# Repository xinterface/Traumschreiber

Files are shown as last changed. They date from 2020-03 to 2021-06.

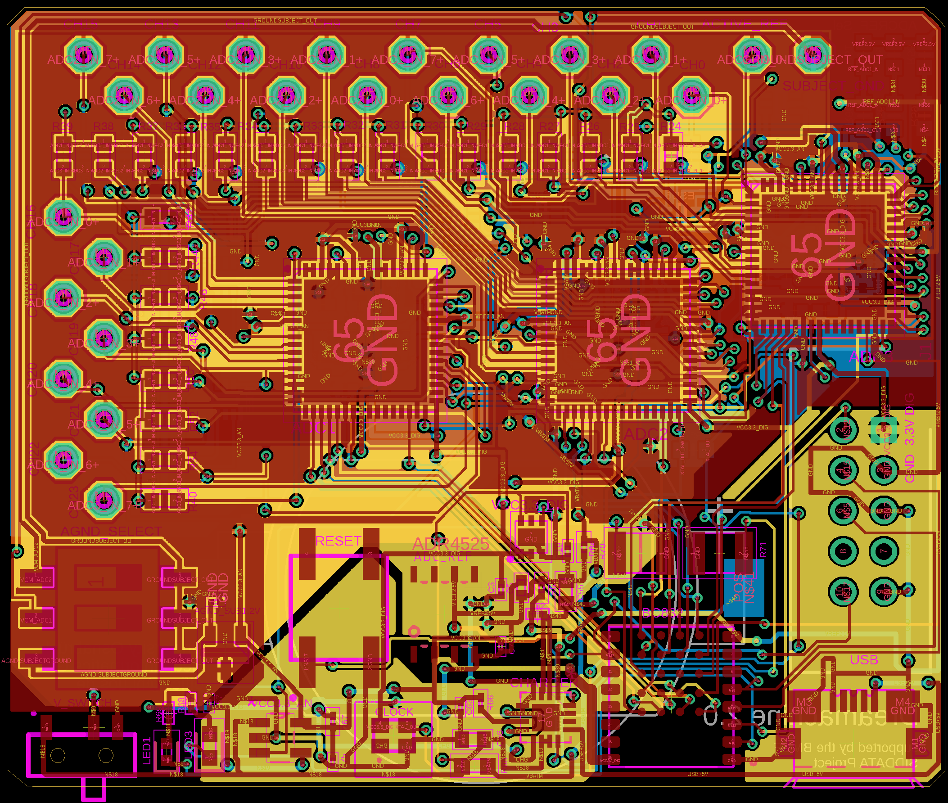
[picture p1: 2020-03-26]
Board_Design/Design_V2.1 - Final/d/Board2.0.png

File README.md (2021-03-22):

# Traumschreiber
Repository of the Traumschreiber and all affiliated projects and theses

## Thus far, this includes:

- A collection of theses
- The repos of the two projects concerned with App Design for the Traumschreiber. More information [on EEGDroid](https://github.com/neuroinfo-os/Traumschreiber/blob/master/Theses/App%20Development/RojasCampos_AppRecordStoreManageEEG.pdf) and on [Traumschreiber mobile EEG](https://github.com/neuroinfo-os/Traumschreiber/blob/master/Theses/Event%20Related%20Potentials/Vidal_AuditoryEvokedPotentials.pdf)
- A collection of operation manuals of the hardware components
- In Progress: Streaming implementation
- In Progress: Embedded System and BLE
# Traumschreiber's List (Version 2.8) + (Version EEG_v2_92_X25)
https://docs.google.com/spreadsheets/d/1prQXEEBJC7Lh-TTywT1AkwJn4IeFenbX4uT630RnToc/edit#gid=0

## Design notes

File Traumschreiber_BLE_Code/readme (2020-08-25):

Compilation and programming the Traumschreiber were tested with Segger Embedded Studio (SES).
https://www.segger.com/downloads/embedded-studio

for compiling one needs the Nordic SDK 15.3
https://www.nordicsemi.com/Software-and-tools/Software/nRF5-SDK/Download
(downloading it with only softdevice s132 is sufficient for use with Traumschreiber)

to compile the code:
- store code folder in the SDK folder at:
SDK/examples/ble_peripheral
- open SES
- choose File -> 'open solution' and navigate to:
SDK/examples/ble_peripheral/<code folder>/pca10040/s132/ses/
- and click the .em-file

the main files are
main.c
traumschreiber_service.c/.h
ad_spi.c/.h

to programm the Traumschreiber:
- compile the project in SES (I use the key F7, should show two partly green bars on the bottom when finished)
- connect the programming board and connect the Traumschreiber to that one with the grey 10-Pin-Connector
- switch the Traumschreiber on!!!!
- use 'Target' -> 'Connect J-Link'
- use 'Target' -> 'Download ble_app_...'
during programming the Traumschreiber LEDs should be off. when finished it should be on.

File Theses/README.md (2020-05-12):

# Traumschreiber
The Traumschreiber system is the subject of several theses covering different research areas within Cognitive Science and Neuroinformatics. Here, the theses are collected. The following gives a brief summary of the individual projects.

#### _The Traumschreiber System - Enabling Crowd-based, Automated, Complex, Polysomnographic Sleep and Dream Experiments_ - K. Appel, Dissertation

In this dissertation the development of the Traumschreiber System as well as its evaluation is presented. The high-tech sleep mask was developed to enable naive crowd
subjects to perform complex polysomnographic sleep and dream experiments at home. It is shown that on the one hand the quality of polysomnographic data recording – including measurements of EEG, EOG, EMG and ECG–, can compete with commercial medical sleep laboratory systems. On the other hand, it was shown with two field studies that even novice subjects can conduct sleep experiment at their homes with the Traumschreiber.

## App Development

#### _Design and implementation of an Android app to  record, store and manage EEG signals_ - R. A. Rojas Campos, Master's Thesis (August 2019)

This thesis describes the most advanced Traumschreiber app to date. With the Android app, the user can collect, plot, save, manage, and share EEG sessions, recorded with the Traumschreiber system. It furthermore introduces a chatbot expert, used to inform the user about epilepsy and presents general information about epilepsy in a clear and accessible way. The code is available [in this repository](https://github.com/adrocampos/EEG-Droid).

#### _Developing and designing a mediator smartphone application for portable sleep EEG recording and biofeedback with focus on the end user experience_ - M. Jäkel, Bachelor's Thesis (February 2017)

This thesis reports on the implementation of a prototype Android application that introduces users to the sleep mask. With the app, users can, among other, connect the Traumschreiber via Bluetooth to their phones, enabling them to visualize recorded EEG data.

## Detection of Event Related Potentials with the Traumschreiber

#### _Studying Neural Correlates of Mind Wandering with Mobile EEG_ - M. Bammel, Bachelor's Thesis (April 2020)

This thesis constitutes a replication of a study by Braboszez and Delorme (2011) who identified neural markers of low alertness during mind wandering with the Traumschreiber. The experiments expose a significantly decreased alpha and beta frequency band power during mind wandering. However, the replication demonstrates that studying higher cognitive functions in a mobile setup using the Traumschreiber does not yield equivalent results compared to a stationary research graded EEG system. The full sourcecode of the project is available [in the author's repository](https://github.com/mbammel/BscThesis).

#### _Auditory Evoked Potentials with Mobile EEG_ - M. Vidal De Palol, Master's Thesis (March 2019)

This project combines the development of an Android App for real-time EEG visualization and recording and an experiment to assess the capability of the device for recording Auditory Evoked Potentials.

#### _Measuring vMMN, P300 and AEPs with a mobile EEG system_ - M. Reimann, Bachelor's Thesis (September 2018)

Within this thesis the potential of the Traumschreiber as mobile EEG system is explored by evaluating its usability and ability to detect event-related potentials (ERP). It is shown that the device is able to produce good and very good results for the ERP under consideration.

#### _Analyzing event-related potentials in 8-channel EEG data using machine learning methods_ - A.-K. Schalkamp, Bachelor's Thesis (September 2018)

This thesis describes a study performed to evaluate whether EEG data acquired with the Traumschreiber can be used with traditional and single-trial analysis. Furthermore, it expands on the importance of electrode placement.

## Eye Position and Gaze Estimation

#### _Eye gaze estimation and gesture recognition using mobile EEG, An application for sleep communication_ - V. Amo Olea, Master's Thesis (September 2019)

Within this project a real-time eye-gaze estimation and gesture recognition
system using Electrooculography (EOG) was developed. A Convolutional Neural Net was trained to recognize eye-typing gestures and three command gestures from movement with closed eyes.

#### _Extracting Eye Positions from Electrooculographic Recordings Using a Machine Learning Approach_ - F. Laubisch, Bachelor's Thesis (September 2016)

In this thesis the relationship between EOG data provided by the Traumschreiber and eye position obtained with a wearable eye tracking device is assessed. It is shown that the sole EOG data is not yet sufficient to produce reliable eye tracking information.

## Sleep and Lucid Dreaming Research

#### _Conducting a Polysomnographic, Automated Auditory Stimulation Sleep Experiment Using a Portable High-Tech Sleep Mask_ - L.S. Mandt, Bachelor's Thesis (April 2017)
The field study discussed in this thesis evaluates the portable high-tech sleep mask for home-based sleep experiments using polysomnography. Additionally, it examines whether the arousal threshold of individual participants can be determined by exposing them to auditory stimulation during the night.

#### _The Scienticity of Lucid Dream Research - A Theoretical and Empirical Approach_ - K. Lüth, Bachelor's Thesis (July 2015)

This work discusses the science-theoretical and historical background of lucid dream research. It presents a survey concerned with the attitude the public has towards the field. The survey showed that the public has a positive opinion.

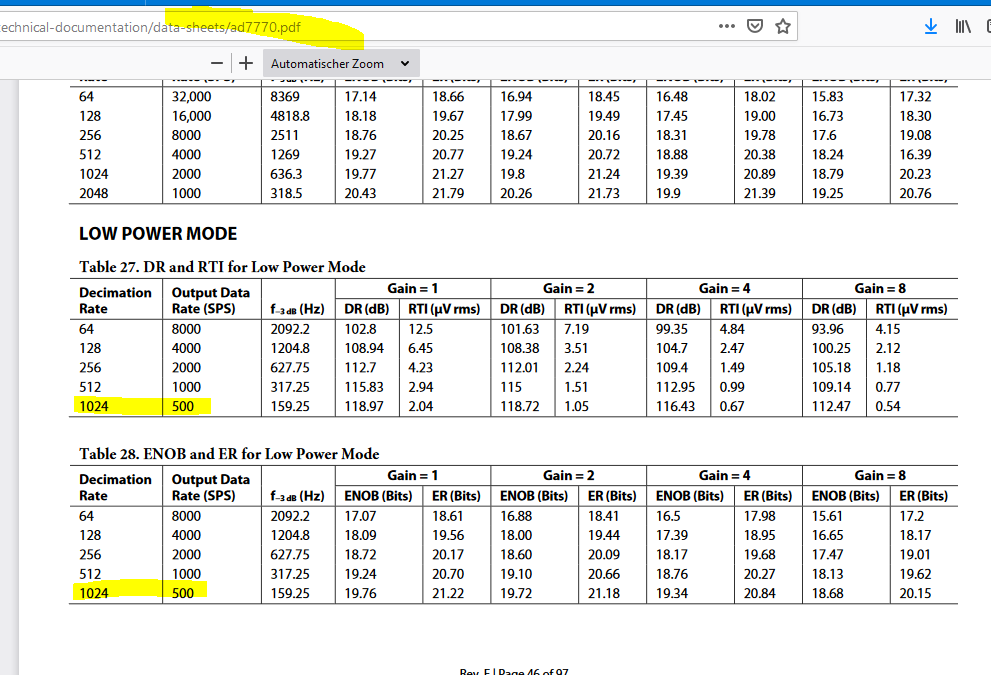
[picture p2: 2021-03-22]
Board_Design/Design_V3.10/PDFs/7770_decimation_rate.PNG

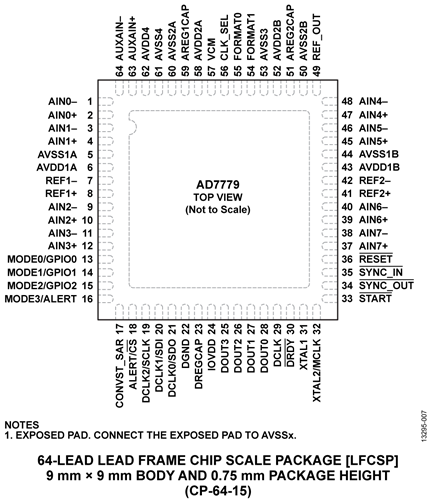
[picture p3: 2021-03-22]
Board_Design/Design_V3.10/PDFs/AD7779-pc.png

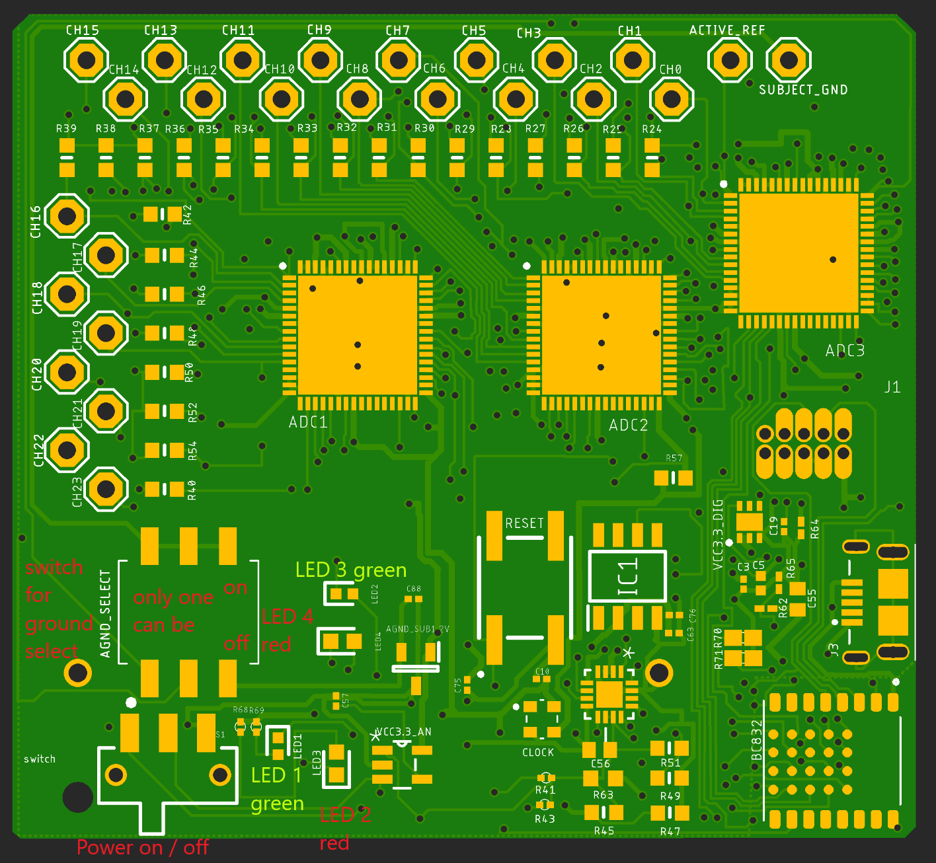
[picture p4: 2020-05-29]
Board_Design/Design_V2.9x/board-explain.png

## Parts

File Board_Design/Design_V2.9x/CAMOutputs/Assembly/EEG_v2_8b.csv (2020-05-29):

Qty | Value | Device | Package | Parts | Description | ALLIED_NUMBER | ALLIED_PRICE-STOCK | AVAILABILITY | CENTERLINE_PITCH | COMMENT | DESCRIPTION | HEIGHT | MANUFACTURER_NAME | MANUFACTURER_PART_NUMBER | MF | MOUSER_PART_NUMBER | MOUSER_PRICE-STOCK | MP | MPN | NUMBER_OF_POSITIONS | OC_FARNELL | OC_NEWARK | PACKAGE | POPULARITY | PRICE | PRODUCT_TYPE | RS_PART_NUMBER | RS_PRICE-STOCK | SUPPLIER | TE_PURCHASE_URL
58 | 0 Ohm | CRCW06030000Z0EAC | RESC1608X55N | R1, R2, R3, R4, R5, R6, R7, R8, R9, R10, R11, R12, R13, R14, R15, R16, R17, R18, R19, R20, R21, R22, R23, R24, R25, R26, R27, R28, R29, R30, R31, R32, R33, R34, R35, R36, R37, R38, R39, R40, R42, R44, R45, R46, R47, R48, R49, R50, R51, R52, R54, R55, R56, R57, R58, R59, R60, R61 | Thick Film Resistors - SMD |  |  |  |  |  | Thick Film Resistors - SMD | 0.55mm | Vishay | CRCW06030000Z0EAC |  | 71-CRCW06030000Z0EAC | https://www.mouser.com/Search/Refine.aspx?Keyword=71-CRCW06030000Z0EAC
2 | 0.01uF | GRM033R61E103MA12J | CAPC0603X33N | C10, C57 | Multilayer Ceramic Capacitors MLCC - SMD/SMT 0201 0.01uF 25volts *Derate Voltage/Temp |  |  |  |  |  | Multilayer Ceramic Capacitors MLCC - SMD/SMT 0201 0.01uF 25volts *Derate Voltage/Temp | 0.33mm | Murata Electronics | GRM033R61E103MA12J |  | 81-GRM033R61E103MA2J | https://www.mouser.co.uk/ProductDetail/Murata-Electronics/GRM033R61E103MA12J?qs=hNud%2FORuBR1kPmeKqdhtJA%3D%3D
25 | 0.1 uF | LMK063C6104KP-F | CAPC0603X33N | C63, C64, C65, C66, C67, C68, C69, C70, C71, C72, C73, C74, C75, C76, C77, C78, C79, C81, C82, C83, C84, C85, C86, C87, C88 | 0201 (0603M), 0402 (1005M) 100nF MLCC 10V dc +/-10% SMD LMK063C6104KP-F |  |  |  |  |  | 0201 (0603M), 0402 (1005M) 100nF MLCC 10V dc +/-10% SMD LMK063C6104KP-F | 0.33mm | TAIYO YUDEN | LMK063C6104KP-F |  | 963-LMK063C6104KP-F | https://www.mouser.co.uk/ProductDetail/Taiyo-Yuden/LMK063C6104KP-F?qs=vF%252B8ahGVildHIKWi2d6PKQ%3D%3D |  |  |  |  |  |  |  |  |  | 1843409P | http://uk.rs-online.com/web/p/products/1843409P
3 | 1 kohm | RC0201JR-071KL | RESC0603X26N | R41, R43, R69 | YAGEO - RC0201JR-071KL - RES, THICK FILM, 1K, 5%, 0.5W, 0201, REEL |  |  |  |  |  | YAGEO - RC0201JR-071KL - RES, THICK FILM, 1K, 5%, 0.5W, 0201, REEL | 0.26mm | YAGEO (PHYCOMP) | RC0201JR-071KL |  | 603-RC0201JR-071KL | https://www.mouser.co.uk/ProductDetail/Yageo/RC0201JR-071KL?qs=V1yeUXFNrklkaJ2L0z8I%252BA%3D%3D |  |  |  |  |  |  |  |  |  | 1987634 | http://uk.rs-online.com/web/p/products/1987634
31 | 1 uF | JMK105BJ105MP-F | CAPC1005X33N | C1, C2, C4, C5, C6, C7, C8, C9, C11, C12, C13, C14, C15, C16, C17, C18, C21, C24, C25, C26, C27, C28, C29, C30, C31, C32, C37, C38, C39, C40, C51 | Taiyo Yuden JMK105BJ105MP-F 1F MLCC 6.3V dc +/-20% Tolerance SMD |  |  |  |  |  | Taiyo Yuden JMK105BJ105MP-F 1F MLCC 6.3V dc +/-20% Tolerance SMD | 0.33mm | TAIYO YUDEN | JMK105BJ105MP-F |  | 963-JMK105BJ105MP-F | https://www.mouser.com/Search/Refine.aspx?Keyword=963-JMK105BJ105MP-F |  |  |  |  |  |  |  |  |  | 1843471 | https://uk.rs-online.com/web/p/products/1843471
2 | 10 uF | EMK107BBJ106MA-T | CAPC1608X100N | C55, C56 | TAIYO YUDEN - EMK107BBJ106MA-T - CAPACITOR, MLCC, X5R, 10UF, 16V, 0603, REEL |  |  |  |  |  | TAIYO YUDEN - EMK107BBJ106MA-T - CAPACITOR, MLCC, X5R, 10UF, 16V, 0603, REEL | 1mm | TAIYO YUDEN | EMK107BBJ106MA-T |  | 963-EMK107BBJ106MA-T | https://www.mouser.com/Search/Refine.aspx?Keyword=963-EMK107BBJ106MA-T |  |  |  |  |  |  |  |  |  | 1843904P | http://uk.rs-online.com/web/p/products/1843904P
1 | 1051 | 1051 | 1051 | U2 | Cylindrical Battery Contacts, Clips, Holders & Springs THM BATTERY HOLDER CR123A | 71135178 | https://www.alliedelec.com/keystoneelectronics-1051/71135178/ |  |  |  | Cylindrical Battery Contacts, Clips, Holders & Springs THM BATTERY HOLDER CR123A | 15.24mm | Keystone Electronics | 1051 |  | 534-1051 | https://www.mouser.co.uk/ProductDetail/Keystone-Electronics/1051?qs=wOxb8XianXhV6wGCGUD6gA%3D%3D
2 | 150060RS75000 | 150060RS75000 | LEDC1608X80N | LED3, LED4 | WURTH ELEKTRONIK - 150060RS75000 - LED, 0603, RED, 250MCD, 625NM |  |  |  |  |  | WURTH ELEKTRONIK - 150060RS75000 - LED, 0603, RED, 250MCD, 625NM | 0.8mm | Wurth Elektronik | 150060RS75000 |  | 710-150060RS75000 | https://www.mouser.com/Search/Refine.aspx?Keyword=710-150060RS75000 |  |  |  |  |  |  |  |  |  | 8154203P | http://uk.rs-online.com/web/p/products/8154203P
1 | 1kohm | RC0201JR-071KL | RESC0603X26N | R68 | YAGEO - RC0201JR-071KL - RES, THICK FILM, 1K, 5%, 0.5W, 0201, REEL |  |  |  |  |  | YAGEO - RC0201JR-071KL - RES, THICK FILM, 1K, 5%, 0.5W, 0201, REEL | 0.26mm | YAGEO (PHYCOMP) | RC0201JR-071KL |  | 603-RC0201JR-071KL | https://www.mouser.co.uk/ProductDetail/Yageo/RC0201JR-071KL?qs=V1yeUXFNrklkaJ2L0z8I%252BA%3D%3D |  |  |  |  |  |  |  |  |  | 1987634 | http://uk.rs-online.com/web/p/products/1987634
2 | 2.2 kOhms | RC0603JR-072K2L | RESC1608X55N | R70, R71 | RESISTOR, 0603 2.2K Ohms +/-5% 1/10 W |  |  |  |  |  | RESISTOR, 0603 2.2K Ohms +/-5% 1/10 W | 0.55mm | YAGEO (PHYCOMP) | RC0603JR-072K2L |  | 603-RC0603JR-072K2L | https://www.mouser.co.uk/ProductDetail/Yageo/RC0603JR-072K2L?qs=%2F9ZTgpVJnN4N31C%252B33L1Sw%3D%3D
2 | 2.2uF | GRM033R60J225ME47D | CAPC0603X33N | C3, C19 | Multilayer Ceramic Capacitors MLCC - SMD/SMT 0201 2.2uF 6.3volts |  |  |  |  |  | Multilayer Ceramic Capacitors MLCC - SMD/SMT 0201 2.2uF 6.3volts | 0.33mm | Murata Electronics | GRM033R60J225ME47D |  | 81-GRM033R60J225ME7D | https://www.mouser.com/Search/Refine.aspx?Keyword=81-GRM033R60J225ME7D
1 | 200kohm | CRCW0201200KFNED | RESC0603X28N | R62 | VISHAY - CRCW0201200KFNED - RES, THICK FILM, 200K, 1%, 0.05W, 0201 |  |  |  |  |  | VISHAY - CRCW0201200KFNED - RES, THICK FILM, 200K, 1%, 0.05W, 0201 | 0.28mm | Vishay | CRCW0201200KFNED |  | 71-CRCW0201200KFNED | https://www.mouser.co.uk/ProductDetail/Vishay-Dale/CRCW0201200KFNED?qs=4bbongekVIR3iw5xFt9eBQ%3D%3D
1 | 2040002-1 | 2040002-1 | TE_2040002-1 | J3 | Conn USB Type B RCP 5 POS 0.65mm Solder RA SMD 5 Terminal 1 Port T/R |  |  | Unavailable | .65 mm[.025 in] | 2040002-1 | Conn Micro USB 2.0 Type B RCP 5 POS 0.65mm Solder RA SMD 5 Terminal 1 Port T/R |  |  |  | TE Connectivity |  |  | 2040002-1 |  | 5 |  |  | None |  | None | Connector |  |  |  | https://www.te.com/usa-en/product-2040002-1.html?te_bu=Cor&te_type=disp&elqCampaignId=32493
1 | 219-3LPSTR | 219-3LPSTR | 2193LPSTR | AGND_SELECT | 3 Way Surface Mount DIP Switch Single Pole Single Throw (SPST) |  |  |  |  |  | 3 Way Surface Mount DIP Switch Single Pole Single Throw (SPST) | 3.95mm | CTS | 219-3LPSTR |  | 774-2193LPSTR | https://www.mouser.com/Search/Refine.aspx?Keyword=774-2193LPSTR |  |  |  |  |  |  |  |  |  | 1774327 | http://uk.rs-online.com/web/p/products/1774327
2 | 41.2 kOhms | CRCW020141K2FNED | RESC0603X28N | R64, R65 | Thick Film Resistors - SMD 41.2K OHM 1% |  |  |  |  |  | Thick Film Resistors - SMD 41.2K OHM 1% | 0.28mm | Vishay | CRCW020141K2FNED |  | 71-CRCW020141K2FNED | https://www.mouser.com/Search/Refine.aspx?Keyword=71-CRCW020141K2FNED
1 | 82kOhms | ERA-3AEB823V | RESC1608X55N | R63 | RESISTOR, 0603 82 kOhm +/-0.1% 0.1 W |  |  |  |  |  | RESISTOR, 0603 82 kOhm +/-0.1% 0.1 W | 0.55mm | Panasonic | ERA-3AEB823V |  | 667-ERA-3AEB823V | https://www.mouser.com/Search/Refine.aspx?Keyword=667-ERA-3AEB823V
3 | AD7771BCPZ | AD7771BCPZ | QFN50P900X900X80-65N | ADC1, ADC2, ADC3 | Analog to Digital Converters - ADC Eight 24B 128ksps SD-ADC PGA SRC |  |  |  |  |  | Analog to Digital Converters - ADC Eight 24B 128ksps SD-ADC PGA SRC | 0.8mm | Analog Devices | AD7771BCPZ |  | 584-AD7771BCPZ | https://www.mouser.com/Search/Refine.aspx?Keyword=584-AD7771BCPZ
1 | ADP7118ACPZN3.3-R7 | ADP7118ACPZN3.3-R7 | SON65P200X200X65-7N | VCC3.3_DIG | LDO Voltage Regulators 20V 200mA LDO 3.3Vo |  |  |  |  |  | LDO Voltage Regulators 20V 200mA LDO 3.3Vo | 0.65mm | Linear Technology | ADP7118ACPZN3.3-R7 |  | 584-P7118ACPZN3.3R7 | https://www.mouser.com/Search/Refine.aspx?Keyword=584-P7118ACPZN3.3R7
1 | ADR4525ARZ | ADR4525ARZ | SOIC127P600X175-8N | IC1 | Analog Devices, ADR4525ARZ Analog Devices ADR4525ARZ, Series Voltage Reference 2.5V, /-0.02% 15 V max., 8-Pin SOIC |  |  |  |  |  | Analog Devices, ADR4525ARZ Analog Devices ADR4525ARZ, Series Voltage Reference 2.5V, /-0.02% 15 V max., 8-Pin SOIC | 1.75mm | Analog Devices | ADR4525ARZ |  | 584-ADR4525ARZ | https://www.mouser.co.uk/ProductDetail/Analog-Devices/ADR4525ARZ?qs=WIvQP4zGangC7PeS%252B5s%2F2Q%3D%3D |  |  |  |  |  |  |  |  |  | 8023880P | http://uk.rs-online.com/web/p/products/8023880P
1 | BC832 | BC832 | XCVR_BC832 | BC832 | Micro BLE 5 Module: Nordic nRF52832 SoC with chip antenna and castellated pins |  |  | Unavailable |  |  | Bluetooth Bluetooth v5.0 Transceiver Module 2.4GHz Integrated, Chip Surface Mount |  |  |  | Fanstel Corp. |  |  | BC832 |  |  |  |  | Module Fanstel Corp. |  | None
1 | BQ24072TRGTR | BQ24072TRGTR | QFN50P300X300X100-17N | CHARGER | 1.5A USB-Friendly Li-Ion Battery Charger and Power-Path Management IC |  |  |  |  |  |  |  |  |  |  |  |  |  | BQ24072TRGTR |  | - | 74R6078 | QFN-16 |  |  |  |  |  | Texas Instruments
1 | DSC1001DI5-008.1920T | DSC1001DI5-008.1920T | DSC1001DI50081920T | CLOCK | Standard Clock Oscillators MEMS Oscillator, Low Power, -40C-85C, 10ppm 1.8V-3.3V Low-Power Precision CMOS Oscillators |  |  |  |  |  | Standard Clock Oscillators MEMS Oscillator, Low Power, -40C-85C, 10ppm 1.8V-3.3V Low-Power Precision CMOS Oscillators | 0.85mm | Microchip | DSC1001DI5-008.1920T |  | 998-1001DI5008.1920T | https://www.mouser.co.uk/ProductDetail/Microchip-Technology-Micrel/DSC1001DI5-0081920T?qs=moDRE%2FDosU0uLfPLWfhb9w%3D%3D
1 | EVQ-Q2B03W | EVQ-Q2B03W | EVQQ2 | RESET | PANASONIC ELECTRONIC COMPONENTS - EVQ-Q2B03W - SWITCH, TACTILE, SPST-NO, 20mA, 15VDC, SMD | 70270748 | https://www.alliedelec.com/panasonic-evq-q2b03w/70270748/ |  |  |  | PANASONIC ELECTRONIC COMPONENTS - EVQ-Q2B03W - SWITCH, TACTILE, SPST-NO, 20mA, 15VDC, SMD | mm | Panasonic | EVQ-Q2B03W |  | 667-EVQ-Q2B03W | https://www.mouser.com/Search/Refine.aspx?Keyword=667-EVQ-Q2B03W
1 | ISL21010DFH312Z-TK | ISL21010DFH312Z-TK | SOT95P237X112-3N | AGND_SUB1.2V | Voltage References Micropower Voltage Reference |  |  |  |  |  | Voltage References Micropower Voltage Reference | 1.12mm | Renesas Electronics | ISL21010DFH312Z-TK |  | 968-ISL21010DFH312ZT | https://www.mouser.com/Search/ProductDetail.aspx?qs=9fLuogzTs8LVsLxgRfQnrw%3d%3d
1 | JS102011SAQN | JS102011SAQN | JS102011SAQN | S1 | C & K COMPONENTS - JS102011SAQN - SWITCH, SPDT, 0.6A, 6VDC, SIDE, SMD | 71173976 | https://www.alliedelec.com/c-k-js102011saqn/71173976/ |  |  |  | C & K COMPONENTS - JS102011SAQN - SWITCH, SPDT, 0.6A, 6VDC, SIDE, SMD | mm | C & K COMPONENTS | JS102011SAQN |  | 611-JS102011SAQN | https://www.mouser.com/Search/Refine.aspx?Keyword=611-JS102011SAQN |  |  |  |  |  |  |  |  |  | 1543603 | http://uk.rs-online.com/web/p/products/1543603
26 | SE11 | SE11 | SE11 | ACTIVE_REF, CH0, CH1, CH2, CH3, CH4, CH5, CH6, CH7, CH8, CH9, CH10, CH11, CH12, CH13, CH14, CH15, CH16, CH17, CH18, CH19, CH20, CH21, CH22, CH23, SUBJECT_GND | SOLDER PAD RTM, drill 1,1mm, distributor Buerklin, 07F810 |  |  |  |  |  |  |  |  |  |  |  |  |  |  |  |  |  |  | 2
1 | SHF-105-01-L-D-TH-TR | SHF-105-01-L-D-TH-TR | SHF10501LDTHTR | J1 | Headers & Wire Housings .050 Shrouded Terminal Strip For FFSD" |  |  |  |  |  | Headers & Wire Housings .050 Shrouded Terminal Strip For FFSD" | 5.33mm | SAMTEC | SHF-105-01-L-D-TH-TR |  | 200-SHF10501LDTHTR | https://www.mouser.co.uk/ProductDetail/Samtec/SHF-105-01-L-D-TH-TR?qs=%252BZP6%2F%252BtExtDFuyepp9uTfQ%3D%3D
2 | SML-P11MTT86R | SML-P11MTT86R | LEDC1006X25N | LED1, LED2 | ROHM - SML-P11MTT86R - LED, YELLOW GREEN, 2.1MCD, 569NM, 0402 |  |  |  |  |  | ROHM - SML-P11MTT86R - LED, YELLOW GREEN, 2.1MCD, 569NM, 0402 | 0.25mm | ROHM Semiconductor | SML-P11MTT86R |  | 755-SML-P11MTT86R | https://www.mouser.com/Search/Refine.aspx?Keyword=755-SML-P11MTT86R
7 | TPD4E1B06DRLR | TPD4E1B06DRLR | SOP50P160X60-6N | ESD1, ESD2, ESD3, ESD4, ESD5, ESD6, ESD7 | Bidirectional Quad-Channel High-Speed ESD Protection Device |  |  |  |  |  | Bidirectional Quad-Channel High-Speed ESD Protection Device | 0.6mm | Texas Instruments | TPD4E1B06DRLR |  | 595-TPD4E1B06DRLR | https://www.mouser.com/Search/Refine.aspx?Keyword=595-TPD4E1B06DRLR
1 | TPS73233DBVT | TPS73233DBVT | SOT95P280X145-5N | VCC3.3_AN | Cap-Free, NMOS, 250mA Low Dropout Regulator with Reverse Current Protection |  |  |  |  |  |  |  |  |  |  |  |  |  | TPS73233DBVT |  | - | 87H2968 | SOT-23-5 |  |  |  |  |  | Texas Instruments

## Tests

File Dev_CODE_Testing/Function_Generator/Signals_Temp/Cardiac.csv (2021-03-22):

data lenth | 16384
frequency | 1000.000000000
amp | 4.000000000
offset | 0.000000000
phase | 0.000000000
xpos | value
0.000000e+000 | 0.00000
6.103516e-008 | 0.00562
1.220703e-007 | 0.00562
1.831055e-007 | 0.00562
2.441406e-007 | 0.00562
3.051758e-007 | 0.00562
3.662109e-007 | 0.00562
4.272461e-007 | 0.00562
4.882813e-007 | 0.00562
5.493164e-007 | 0.00562
6.103515e-007 | 0.00562
6.713867e-007 | 0.00562
7.324219e-007 | 0.00562
7.934570e-007 | 0.00562
8.544922e-007 | 0.00562
9.155273e-007 | 0.00562
9.765625e-007 | 0.00562
1.037598e-006 | 0.00562
1.098633e-006 | 0.00562
1.159668e-006 | 0.00562
1.220703e-006 | 0.00562
1.281738e-006 | 0.00562
1.342773e-006 | 0.00562
1.403809e-006 | 0.00562
1.464844e-006 | 0.00562
1.525879e-006 | 0.00562
1.586914e-006 | 0.00562
1.647949e-006 | 0.00562
1.708984e-006 | 0.00562
1.770019e-006 | 0.00562
1.831055e-006 | 0.00562
1.892090e-006 | 0.00562
1.953125e-006 | 0.00562
2.014160e-006 | 0.00562
2.075195e-006 | 0.00562
2.136230e-006 | 0.00562
2.197266e-006 | 0.00562
2.258301e-006 | 0.00562
2.319336e-006 | 0.00562
2.380371e-006 | 0.00562
2.441406e-006 | 0.00562
2.502441e-006 | 0.00562
2.563477e-006 | 0.00562
2.624512e-006 | 0.00562
2.685547e-006 | 0.00562
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

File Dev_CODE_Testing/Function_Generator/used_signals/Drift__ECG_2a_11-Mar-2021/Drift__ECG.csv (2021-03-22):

data lenth | 16384
frequency | 0.009766
amp | 1.000000000
offset | 0.000000000
phase | 0.000000000
xpos | value
0.000000e+00 | 0.04140
6.103516e-08 | 0.04539
1.220703e-07 | 0.04863
1.831055e-07 | 0.05083
2.441406e-07 | 0.05166
3.051758e-07 | 0.05096
3.662109e-07 | 0.04886
4.272461e-07 | 0.04568
4.882813e-07 | 0.04202
5.493164e-07 | 0.03876
6.103515e-07 | 0.03650
6.713867e-07 | 0.03572
7.324219e-07 | 0.03677
7.934570e-07 | 0.03968
8.544922e-07 | 0.04403
9.155273e-07 | 0.04946
9.765625e-07 | 0.05547
1.037598e-06 | 0.06148
1.098633e-06 | 0.06691
1.159668e-06 | 0.07126
1.220703e-06 | 0.07376
1.281738e-06 | 0.07389
1.342773e-06 | 0.07176
1.403809e-06 | 0.06769
1.464844e-06 | 0.06218
1.525879e-06 | 0.05618
1.586914e-06 | 0.05075
1.647949e-06 | 0.04640
1.708984e-06 | 0.04345
1.770019e-06 | 0.04203
1.831055e-06 | 0.04202
1.892090e-06 | 0.04310
1.953125e-06 | 0.04509
2.014160e-06 | 0.04750
2.075195e-06 | 0.04975
2.136230e-06 | 0.05134
2.197266e-06 | 0.05192
2.258301e-06 | 0.05111
2.319336e-06 | 0.04890
2.380371e-06 | 0.04562
2.441406e-06 | 0.04175
2.502441e-06 | 0.03787
2.563477e-06 | 0.03458
2.624512e-06 | 0.03237
2.685547e-06 | 0.03156
2.746582e-06 | 0.03228
2.807617e-06 | 0.03409
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

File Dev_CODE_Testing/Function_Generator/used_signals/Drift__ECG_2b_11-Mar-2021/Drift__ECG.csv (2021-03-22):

data lenth | 16384
frequency | 0.009766
amp | 1.000000000
offset | 0.000000000
phase | 0.000000000
xpos | value
0.000000e+00 | 0.20698
6.103516e-08 | 0.21163
1.220703e-07 | 0.21487
1.831055e-07 | 0.21718
2.441406e-07 | 0.21830
3.051758e-07 | 0.21786
3.662109e-07 | 0.21602
4.272461e-07 | 0.21309
4.882813e-07 | 0.21012
5.493164e-07 | 0.20912
6.103515e-07 | 0.21078
6.713867e-07 | 0.21556
7.324219e-07 | 0.22385
7.934570e-07 | 0.23534
8.544922e-07 | 0.24842
9.155273e-07 | 0.26261
9.765625e-07 | 0.27735
1.037598e-06 | 0.29209
1.098633e-06 | 0.30625
1.159668e-06 | 0.31933
1.220703e-06 | 0.32882
1.281738e-06 | 0.33250
1.342773e-06 | 0.33051
1.403809e-06 | 0.32315
1.464844e-06 | 0.31091
1.525879e-06 | 0.29621
1.586914e-06 | 0.28205
1.647949e-06 | 0.26897
1.708984e-06 | 0.25726
1.770019e-06 | 0.24711
1.831055e-06 | 0.23837
1.892090e-06 | 0.23081
1.953125e-06 | 0.22547
2.014160e-06 | 0.22218
2.075195e-06 | 0.22045
2.136230e-06 | 0.21972
2.197266e-06 | 0.21962
2.258301e-06 | 0.21861
2.319336e-06 | 0.21623
2.380371e-06 | 0.21277
2.441406e-06 | 0.20873
2.502441e-06 | 0.20465
2.563477e-06 | 0.20119
2.624512e-06 | 0.19881
2.685547e-06 | 0.19780
2.746582e-06 | 0.19835
2.807617e-06 | 0.19872
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

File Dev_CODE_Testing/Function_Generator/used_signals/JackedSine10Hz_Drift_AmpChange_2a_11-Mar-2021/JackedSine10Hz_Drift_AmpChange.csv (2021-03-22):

data lenth | 16384
frequency | 0.009766
amp | 1.000000000
offset | 0.000000000
phase | 0.000000000
xpos | value
0.000000e+00 | 0.00000
6.103516e-08 | 0.00000
1.220703e-07 | 0.00000
1.831055e-07 | 0.00000
2.441406e-07 | 0.00000
3.051758e-07 | 0.00000
3.662109e-07 | 0.00000
4.272461e-07 | 0.00000
4.882813e-07 | 0.00000
5.493164e-07 | -0.00000
6.103515e-07 | -0.00000
6.713867e-07 | -0.00000
7.324219e-07 | -0.00000
7.934570e-07 | -0.00000
8.544922e-07 | 0.00000
9.155273e-07 | 0.00000
9.765625e-07 | 0.00000
1.037598e-06 | 0.00000
1.098633e-06 | 0.00000
1.159668e-06 | 0.00000
1.220703e-06 | 0.00000
1.281738e-06 | 0.00000
1.342773e-06 | 0.00000
1.403809e-06 | 0.00000
1.464844e-06 | 0.00000
1.525879e-06 | -0.00000
1.586914e-06 | -0.00000
1.647949e-06 | -0.00000
1.708984e-06 | -0.00000
1.770019e-06 | -0.00000
1.831055e-06 | 0.00000
1.892090e-06 | 0.00000
1.953125e-06 | 0.00000
2.014160e-06 | 0.00000
2.075195e-06 | 0.00000
2.136230e-06 | 0.00000
2.197266e-06 | 0.00000
2.258301e-06 | 0.00000
2.319336e-06 | 0.00000
2.380371e-06 | 0.00000
2.441406e-06 | 0.00000
2.502441e-06 | -0.00000
2.563477e-06 | -0.00000
2.624512e-06 | -0.00000
2.685547e-06 | -0.00000
2.746582e-06 | -0.00000
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

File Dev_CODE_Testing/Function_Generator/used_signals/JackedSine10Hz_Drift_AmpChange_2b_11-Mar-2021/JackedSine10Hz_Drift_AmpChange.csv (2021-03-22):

data lenth | 16384
frequency | 0.009766
amp | 1.000000000
offset | 0.000000000
phase | 0.000000000
xpos | value
0.000000e+00 | 0.00000
6.103516e-08 | 0.00000
1.220703e-07 | 0.00000
1.831055e-07 | 0.00000
2.441406e-07 | 0.00000
3.051758e-07 | 0.00000
3.662109e-07 | 0.00000
4.272461e-07 | 0.00000
4.882813e-07 | 0.00000
5.493164e-07 | -0.00000
6.103515e-07 | -0.00000
6.713867e-07 | -0.00000
7.324219e-07 | -0.00000
7.934570e-07 | -0.00000
8.544922e-07 | 0.00000
9.155273e-07 | 0.00000
9.765625e-07 | 0.00000
1.037598e-06 | 0.00000
1.098633e-06 | 0.00000
1.159668e-06 | 0.00000
1.220703e-06 | 0.00000
1.281738e-06 | 0.00000
1.342773e-06 | 0.00000
1.403809e-06 | 0.00000
1.464844e-06 | 0.00000
1.525879e-06 | -0.00000
1.586914e-06 | -0.00000
1.647949e-06 | -0.00000
1.708984e-06 | -0.00000
1.770019e-06 | -0.00000
1.831055e-06 | 0.00000
1.892090e-06 | 0.00000
1.953125e-06 | 0.00000
2.014160e-06 | 0.00000
2.075195e-06 | 0.00000
2.136230e-06 | 0.00000
2.197266e-06 | 0.00000
2.258301e-06 | 0.00000
2.319336e-06 | 0.00000
2.380371e-06 | 0.00000
2.441406e-06 | 0.00000
2.502441e-06 | -0.00000
2.563477e-06 | -0.00000
2.624512e-06 | -0.00000
2.685547e-06 | -0.00000
2.746582e-06 | -0.00000
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

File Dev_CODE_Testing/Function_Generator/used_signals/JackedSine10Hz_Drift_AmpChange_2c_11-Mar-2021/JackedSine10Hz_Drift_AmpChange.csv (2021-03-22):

data lenth | 16384
frequency | 0.009766
amp | 1.000000000
offset | 0.000000000
phase | 0.000000000
xpos | value
0.000000e+00 | 0.00000
6.103516e-08 | 0.00000
1.220703e-07 | 0.00000
1.831055e-07 | 0.00000
2.441406e-07 | 0.00000
3.051758e-07 | 0.00000
3.662109e-07 | 0.00000
4.272461e-07 | 0.00000
4.882813e-07 | 0.00000
5.493164e-07 | -0.00000
6.103515e-07 | -0.00000
6.713867e-07 | -0.00000
7.324219e-07 | -0.00000
7.934570e-07 | -0.00000
8.544922e-07 | 0.00000
9.155273e-07 | 0.00000
9.765625e-07 | 0.00000
1.037598e-06 | 0.00000
1.098633e-06 | 0.00000
1.159668e-06 | 0.00000
1.220703e-06 | 0.00000
1.281738e-06 | 0.00000
1.342773e-06 | 0.00000
1.403809e-06 | 0.00000
1.464844e-06 | 0.00000
1.525879e-06 | -0.00000
1.586914e-06 | -0.00000
1.647949e-06 | -0.00000
1.708984e-06 | -0.00000
1.770019e-06 | -0.00000
1.831055e-06 | 0.00000
1.892090e-06 | 0.00000
1.953125e-06 | 0.00000
2.014160e-06 | 0.00000
2.075195e-06 | 0.00001
2.136230e-06 | 0.00001
2.197266e-06 | 0.00001
2.258301e-06 | 0.00000
2.319336e-06 | 0.00000
2.380371e-06 | 0.00000
2.441406e-06 | 0.00000
2.502441e-06 | -0.00000
2.563477e-06 | -0.00001
2.624512e-06 | -0.00001
2.685547e-06 | -0.00001
2.746582e-06 | -0.00000
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

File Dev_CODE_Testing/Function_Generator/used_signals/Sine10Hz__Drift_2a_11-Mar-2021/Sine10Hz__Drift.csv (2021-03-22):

data lenth | 16384
frequency | 0.009766
amp | 1.000000000
offset | 0.000000000
phase | 0.000000000
xpos | value
0.000000e+00 | 0.00000
6.103516e-08 | 0.00383
1.220703e-07 | 0.00707
1.831055e-07 | 0.00924
2.441406e-07 | 0.01000
3.051758e-07 | 0.00924
3.662109e-07 | 0.00707
4.272461e-07 | 0.00383
4.882813e-07 | 0.00000
5.493164e-07 | -0.00383
6.103515e-07 | -0.00707
6.713867e-07 | -0.00924
7.324219e-07 | -0.01000
7.934570e-07 | -0.00924
8.544922e-07 | -0.00707
9.155273e-07 | -0.00383
9.765625e-07 | -0.00000
1.037598e-06 | 0.00383
1.098633e-06 | 0.00707
1.159668e-06 | 0.00924
1.220703e-06 | 0.01000
1.281738e-06 | 0.00924
1.342773e-06 | 0.00707
1.403809e-06 | 0.00383
1.464844e-06 | 0.00000
1.525879e-06 | -0.00383
1.586914e-06 | -0.00707
1.647949e-06 | -0.00924
1.708984e-06 | -0.01000
1.770019e-06 | -0.00924
1.831055e-06 | -0.00707
1.892090e-06 | -0.00383
1.953125e-06 | -0.00000
2.014160e-06 | 0.00383
2.075195e-06 | 0.00707
2.136230e-06 | 0.00924
2.197266e-06 | 0.01000
2.258301e-06 | 0.00924
2.319336e-06 | 0.00707
2.380371e-06 | 0.00383
2.441406e-06 | 0.00000
2.502441e-06 | -0.00383
2.563477e-06 | -0.00707
2.624512e-06 | -0.00924
2.685547e-06 | -0.01000
2.746582e-06 | -0.00924
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

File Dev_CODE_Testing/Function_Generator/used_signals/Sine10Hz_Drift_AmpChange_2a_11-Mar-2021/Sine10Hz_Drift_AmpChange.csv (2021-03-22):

data lenth | 16384
frequency | 0.009766
amp | 1.000000000
offset | 0.000000000
phase | 0.000000000
xpos | value
0.000000e+00 | 0.00000
6.103516e-08 | 0.00000
1.220703e-07 | 0.00000
1.831055e-07 | 0.00000
2.441406e-07 | 0.00000
3.051758e-07 | 0.00000
3.662109e-07 | 0.00000
4.272461e-07 | 0.00000
4.882813e-07 | 0.00000
5.493164e-07 | -0.00000
6.103515e-07 | -0.00000
6.713867e-07 | -0.00000
7.324219e-07 | -0.00000
7.934570e-07 | -0.00000
8.544922e-07 | -0.00000
9.155273e-07 | -0.00000
9.765625e-07 | -0.00000
1.037598e-06 | 0.00000
1.098633e-06 | 0.00000
1.159668e-06 | 0.00000
1.220703e-06 | 0.00000
1.281738e-06 | 0.00000
1.342773e-06 | 0.00000
1.403809e-06 | 0.00000
1.464844e-06 | 0.00000
1.525879e-06 | -0.00000
1.586914e-06 | -0.00000
1.647949e-06 | -0.00000
1.708984e-06 | -0.00000
1.770019e-06 | -0.00000
1.831055e-06 | -0.00000
1.892090e-06 | -0.00000
1.953125e-06 | -0.00000
2.014160e-06 | 0.00000
2.075195e-06 | 0.00000
2.136230e-06 | 0.00000
2.197266e-06 | 0.00000
2.258301e-06 | 0.00000
2.319336e-06 | 0.00000
2.380371e-06 | 0.00000
2.441406e-06 | 0.00000
2.502441e-06 | -0.00000
2.563477e-06 | -0.00000
2.624512e-06 | -0.00000
2.685547e-06 | -0.00000
2.746582e-06 | -0.00000
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

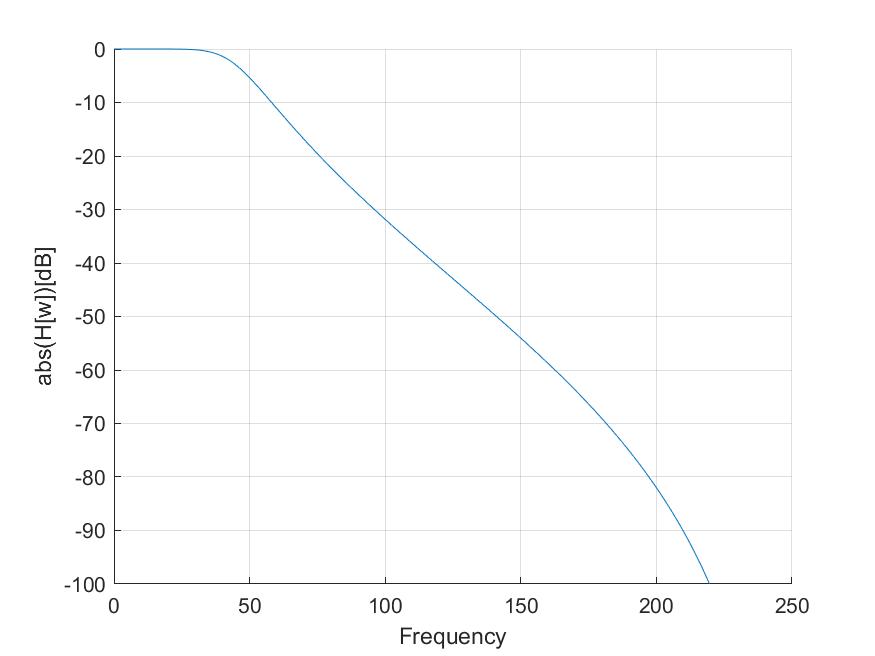
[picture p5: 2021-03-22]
Dev_CODE_Testing/Compression/Filters_DreamMachine_V1_3_11-Mar-2021/FolterCoeff_LowPass_I_fs500_L45_O4.jpg

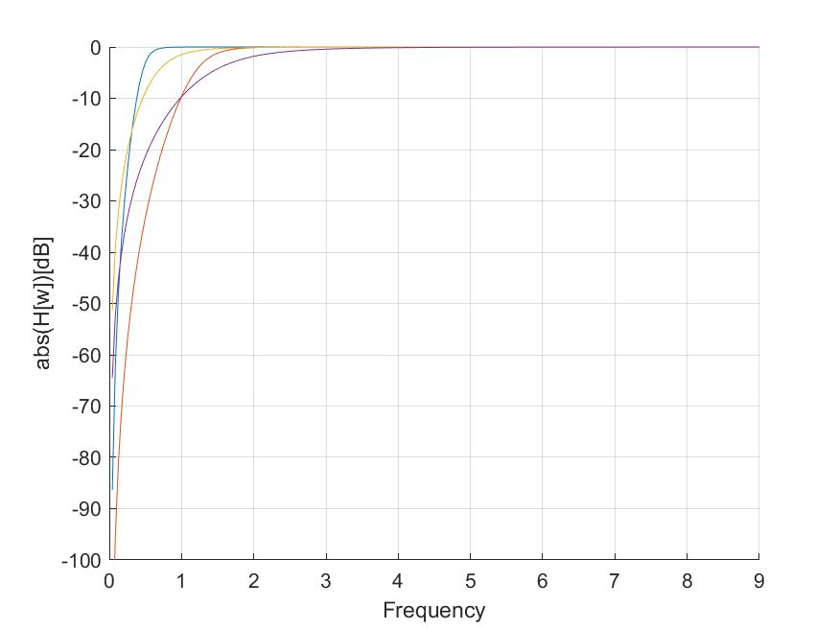
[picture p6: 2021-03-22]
Dev_CODE_Testing/Compression/Filters_DreamMachine_V1_3_11-Mar-2021/FolterCoeff_HighPass_IV_fs167_L1_7_O2.jpg

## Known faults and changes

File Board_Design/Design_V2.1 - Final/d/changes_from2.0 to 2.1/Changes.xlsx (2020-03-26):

 | To Do
1 | Oscilator is wrong frequency. Needs to be 8.192
2 | Correct all points in the BRD
3 | Exchange ADR
4 | exchange clock
5 | exchange battery holder | https://eu.mouser.com/Search/Refine?Keyword=SMTU2477N%e2%80%90LF
6 | exchange usb port | https://eu.mouser.com/Search/Refine?Keyword=ZX62R%e2%80%90B%e2%80%905P
7 | change footprint of the ESD Ics
8
9 | change footprint of832
10
11
12
13
14
15
16
17
18
19
20
21
22
23

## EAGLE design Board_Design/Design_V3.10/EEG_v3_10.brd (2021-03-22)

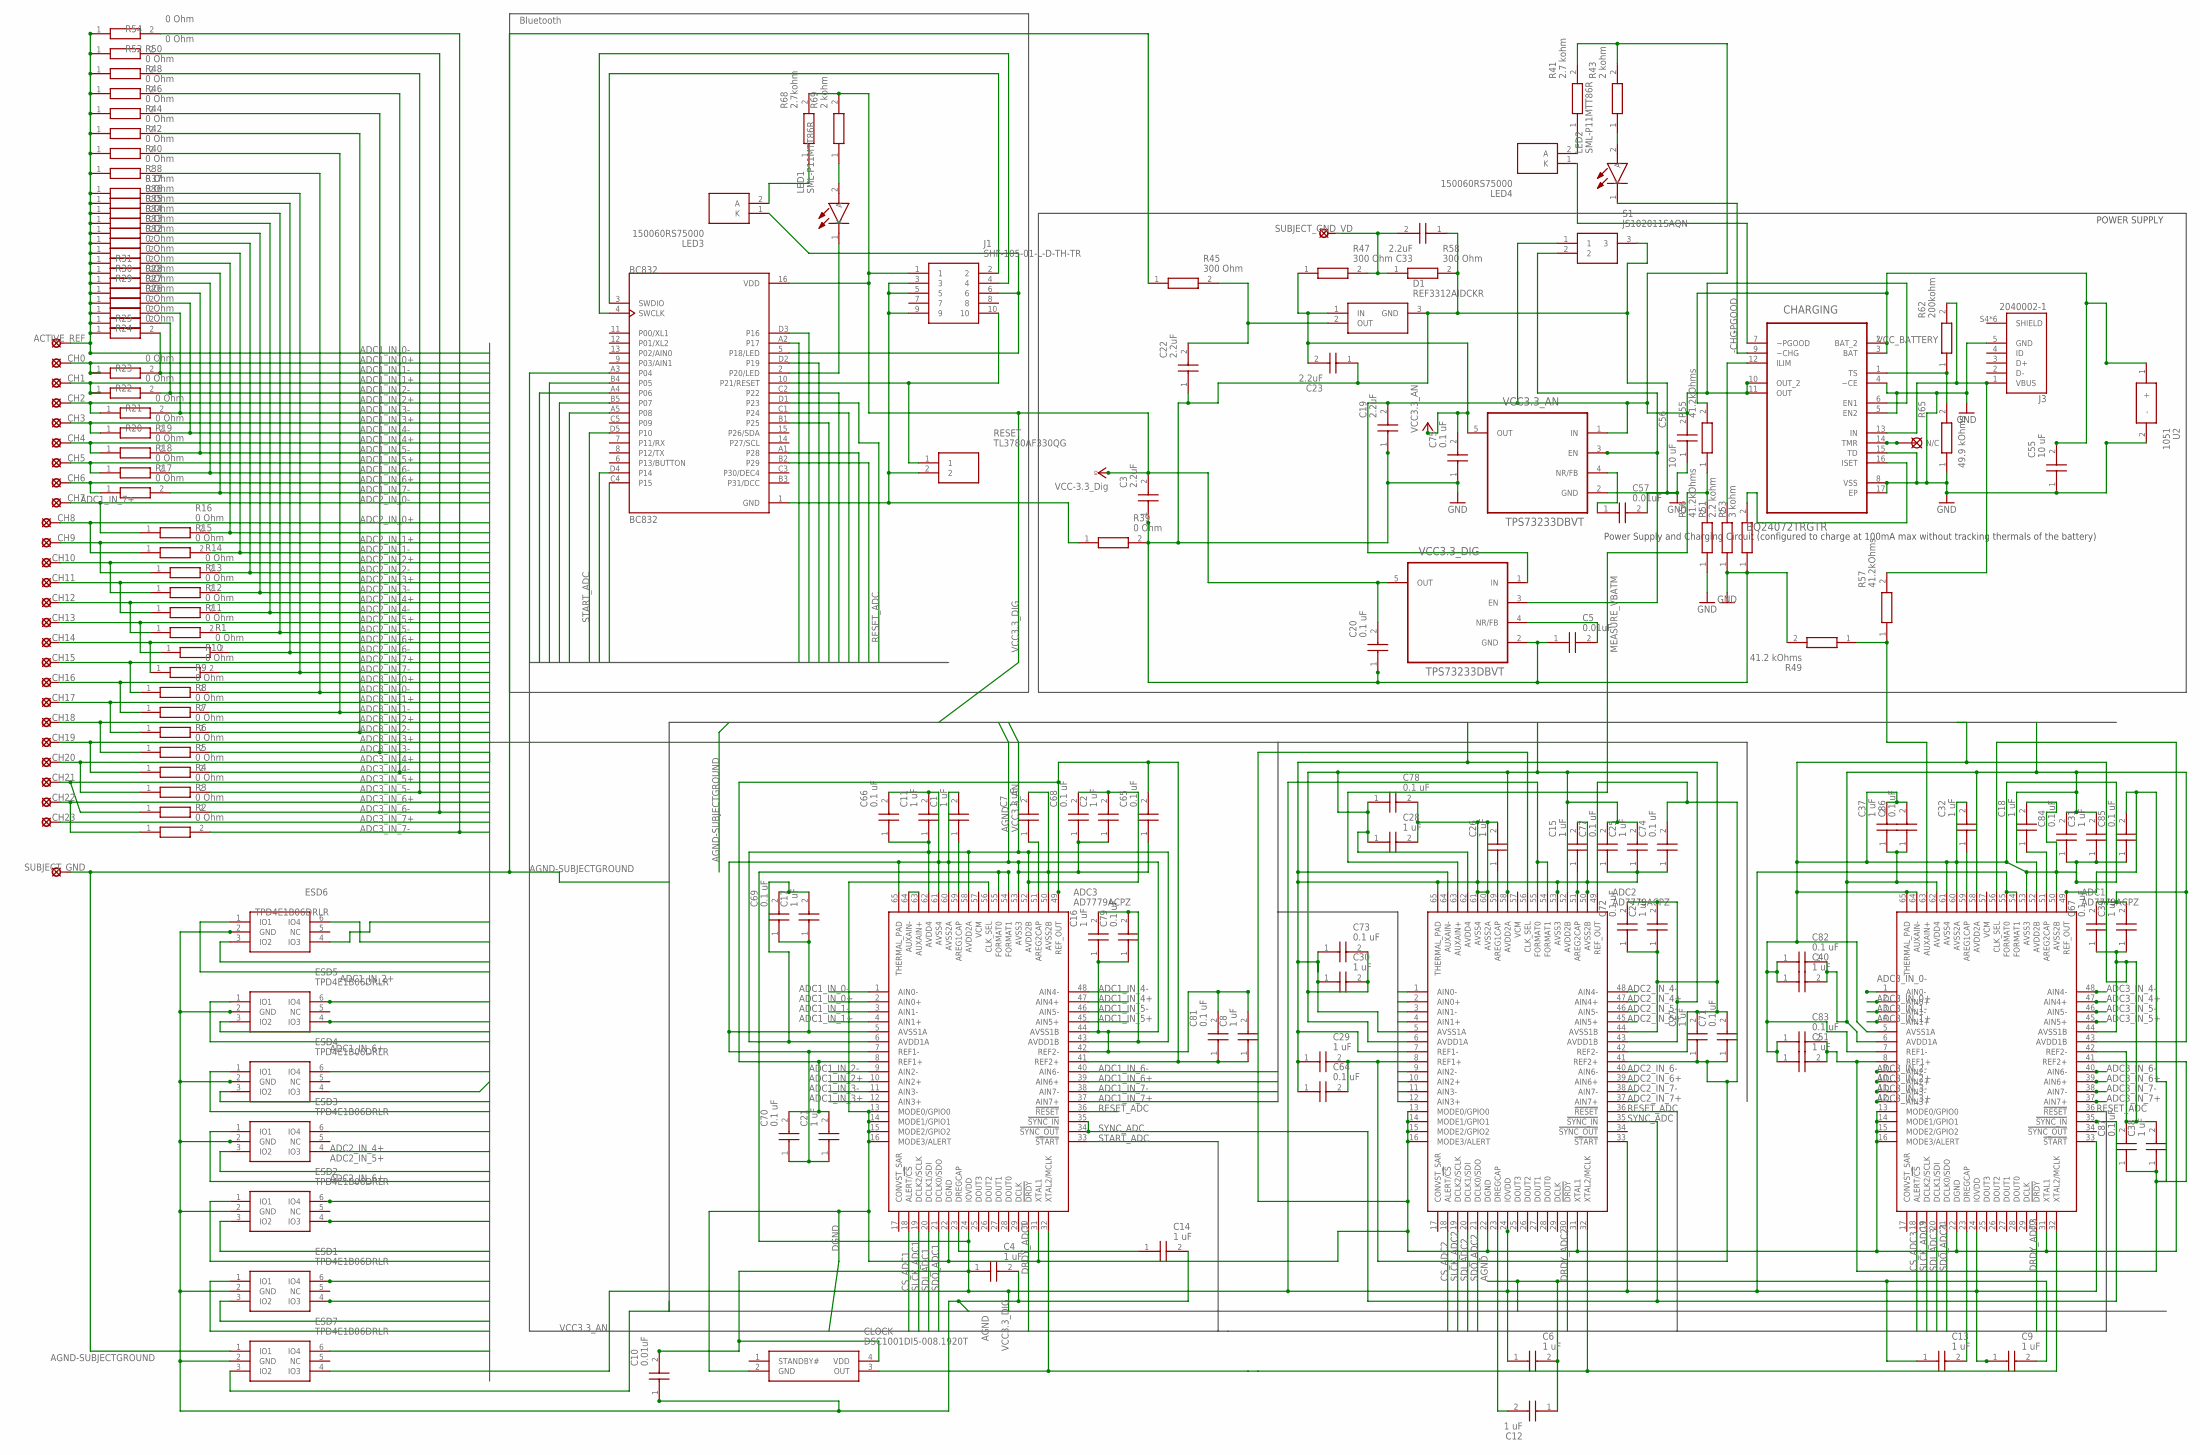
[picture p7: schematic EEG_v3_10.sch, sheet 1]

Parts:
ACTIVE_REF: SE11
ADC1, ADC2, ADC3: AD7779ACPZ; QFN50P900X900X80-65N
BC832: BC832; XCVR_BC832
C1, C2, C4, C6, C7, C8, C9, C11, C12, C13, C14, C15, C16, C17, C18, C21, C24, C25, C26, C27, C28, C29, C30, C31, C32, C37, C38, C39, C40, C51: 1 uF; CAPC1005X33N
C3, C19, C22, C23, C33: 2.2uF; CAPC0603X33N
C5, C10, C57: 0.01uF; CAPC0603X33N
C20, C64, C65, C66, C67, C68, C69, C70, C71, C72, C73, C74, C75, C77, C78, C79, C81, C82, C83, C84, C85, C86, C87: 0.1 uF; CAPC0603X33N
C55, C56: 10 uF; CAPC1608X100N
CH0, CH1, CH2, CH3, CH4, CH5, CH6, CH7, CH8, CH9, CH10, CH11, CH12, CH13, CH14, CH15, CH16, CH17, CH18, CH19, CH20, CH21, CH22, CH23: SE11
CHARGING: BQ24072TRGTR; QFN50P300X300X100-17N
CLOCK: DSC1001DI5-008.1920T; DSC1001DI50081920T
D1: REF3312AIDCKR; SOT65P210X110-3N
ESD1, ESD2, ESD3, ESD4, ESD5, ESD6, ESD7: TPD4E1B06DRLR; SOP50P160X60-6N
J1: SHF-105-01-L-D-TH-TR; SHF10501LDTHTR
J3: 2040002-1; TE_2040002-1
LED1, LED2: SML-P11MTT86R; LEDC1006X25N
LED3, LED4: 150060RS75000; LEDC1608X80N
R1, R2, R3, R4, R5, R6, R7, R8, R9, R10, R11, R12, R13, R14, R15, R16, R17, R18, R19, R20, R21, R22, R23, R24, R25, R26, R27, R28, R29, R30, R31, R32, R33, R34, R35, R36, R37, R38, R39, R40, R42, R44, R46, R48, R50, R52, R54: 0 Ohm; RESC1608X55N
R41: 2.7 kohm; RESC0603X26N
R43, R69: 2 kohm; RESC0603X26N
R45, R47, R58: 300 Ohm; RESC0603X26N
R49: 41.2 kOhms; RESC0603X28N
R51: 2.2 kohm; RESC0603X28N
R53: 3 kohm; RESC0603X26N
R55, R56, R57: 41.2kOhms; RESC0603X28N
R62: 200kohm; RESC0603X28N
R65: 49.9 kOhms; RESC0603X28N
R68: 2.7kohm; RESC0603X26N
RESET: TL3780AF330QG
S1: JS102011SAQN
SUBJECT_GND: SE11
SUBJECT_GND_VD: SE11
U2: 1051
VCC3.3_AN, VCC3.3_DIG: TPS73233DBVT; SOT95P280X145-5N

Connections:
-CHG: CHARGING.9 (~CHG), LED2.1 (K)
-PGOOD: CHARGING.7 (~PGOOD), LED4.1 (K)
ADC1_IN_0+: ADC3.2 (AIN0+), CH0.MP, ESD6.4 (IO3), R23.1
ADC1_IN_0-: ACTIVE_REF.MP, ADC3.1 (AIN0-), ESD6.6 (IO4), R24.1, R25.1, R26.1, R27.1, R28.1, R29.1, R30.1, R31.1, R32.1, R33.1, R34.1, R35.1, R36.1, R37.1, R38.1, R40.1, R42.1, R44.1, R46.1, R48.1, R50.1, R52.1, R54.1
ADC1_IN_1+: ADC3.4 (AIN1+), CH1.MP, ESD6.3 (IO2), R22.1
ADC1_IN_1-: ADC3.3 (AIN1-), R23.2, R24.2
ADC1_IN_2+: ADC3.10 (AIN2+), CH2.MP, ESD6.1 (IO1), R21.1
ADC1_IN_2-: ADC3.9 (AIN2-), R22.2, R25.2
ADC1_IN_3+: ADC3.12 (AIN3+), CH3.MP, ESD5.6 (IO4), R20.1
ADC1_IN_3-: ADC3.11 (AIN3-), R21.2, R26.2
ADC1_IN_4+: ADC3.47 (AIN4+), CH4.MP, ESD5.4 (IO3), R19.1
ADC1_IN_4-: ADC3.48 (AIN4-), R20.2, R27.2
ADC1_IN_5+: ADC3.45 (AIN5+), CH5.MP, ESD5.3 (IO2), R18.1
ADC1_IN_5-: ADC3.46 (AIN5-), R19.2, R28.2
ADC1_IN_6+: ADC3.39 (AIN6+), CH6.MP, ESD5.1 (IO1), R17.1
ADC1_IN_6-: ADC3.40 (AIN6-), R18.2, R29.2
ADC1_IN_7+: ADC3.37 (AIN7+), CH7.MP, ESD4.6 (IO4), R16.1
ADC1_IN_7-: ADC3.38 (AIN7-), R17.2, R30.2
ADC2_IN_0+: ADC2.2 (AIN0+), CH8.MP, ESD4.4 (IO3), R15.1
ADC2_IN_0-: ADC2.1 (AIN0-), R16.2, R31.2
ADC2_IN_1+: ADC2.4 (AIN1+), CH9.MP, ESD4.3 (IO2), R14.1
ADC2_IN_1-: ADC2.3 (AIN1-), R15.2, R32.2
ADC2_IN_2+: ADC2.10 (AIN2+), CH10.MP, ESD4.1 (IO1), R13.1
ADC2_IN_2-: ADC2.9 (AIN2-), R14.2, R33.2
ADC2_IN_3+: ADC2.12 (AIN3+), CH11.MP, ESD3.6 (IO4), R12.1
ADC2_IN_3-: ADC2.11 (AIN3-), R13.2, R34.2
ADC2_IN_4+: ADC2.47 (AIN4+), CH12.MP, ESD3.4 (IO3), R11.1
ADC2_IN_4-: ADC2.48 (AIN4-), R12.2, R35.2
ADC2_IN_5+: ADC2.45 (AIN5+), CH13.MP, ESD3.3 (IO2), R1.1
ADC2_IN_5-: ADC2.46 (AIN5-), R11.2, R36.2
ADC2_IN_6+: ADC2.39 (AIN6+), CH14.MP, ESD3.1 (IO1), R10.1
ADC2_IN_6-: ADC2.40 (AIN6-), R1.2, R37.2
ADC2_IN_7+: ADC2.37 (AIN7+), CH15.MP, ESD2.6 (IO4), R9.1
ADC2_IN_7-: ADC2.38 (AIN7-), R10.2, R38.2
ADC3_IN_0+: ADC1.2 (AIN0+), CH16.MP, ESD2.4 (IO3), R8.1
ADC3_IN_0-: ADC1.1 (AIN0-), R9.2, R40.2
ADC3_IN_1+: ADC1.4 (AIN1+), CH17.MP, ESD2.3 (IO2), R7.1
ADC3_IN_1-: ADC1.3 (AIN1-), R8.2, R42.2
ADC3_IN_2+: ADC1.10 (AIN2+), CH18.MP, ESD2.1 (IO1), R6.1
ADC3_IN_2-: ADC1.9 (AIN2-), R7.2, R44.2
ADC3_IN_3+: ADC1.12 (AIN3+), CH19.MP, ESD1.6 (IO4), R5.1
ADC3_IN_3-: ADC1.11 (AIN3-), R6.2, R46.2
ADC3_IN_4+: ADC1.47 (AIN4+), CH20.MP, ESD1.4 (IO3), R4.1
ADC3_IN_4-: ADC1.48 (AIN4-), R5.2, R48.2
ADC3_IN_5+: ADC1.45 (AIN5+), CH21.MP, ESD1.3 (IO2), R3.1
ADC3_IN_5-: ADC1.46 (AIN5-), R4.2, R50.2
ADC3_IN_6+: ADC1.39 (AIN6+), CH22.MP, ESD1.1 (IO1), R2.1
ADC3_IN_6-: ADC1.40 (AIN6-), R3.2, R52.2
ADC3_IN_7+: ADC1.37 (AIN7+), CH23.MP, ESD7.6 (IO4)
ADC3_IN_7-: ADC1.38 (AIN7-), R2.2, R54.2
AGND: ADC1.5 (AVSS1A), ADC1.7 (REF1-), ADC1.42 (REF2-), ADC1.44 (AVSS1B), ADC1.50 (AVSS2B), ADC1.53 (AVSS3), ADC1.60 (AVSS2A), ADC1.61 (AVSS4), ADC1.64 (AUXAIN-), ADC1.65 (THERMAL_PAD), ADC2.5 (AVSS1A), ADC2.7 (REF1-), ADC2.42 (REF2-), ADC2.44 (AVSS1B), ADC2.50 (AVSS2B), ADC2.53 (AVSS3), ADC2.60 (AVSS2A), ADC2.61 (AVSS4), ADC2.64 (AUXAIN-), ADC2.65 (THERMAL_PAD), ADC3.5 (AVSS1A), ADC3.7 (REF1-), ADC3.42 (REF2-), ADC3.44 (AVSS1B), ADC3.50 (AVSS2B), ADC3.53 (AVSS3), ADC3.60 (AVSS2A), ADC3.61 (AVSS4), ADC3.65 (THERMAL_PAD), C1.2, C2.1, C3.1, C4.2, C5.1, C6.2, C7.2, C8.2, C9.2, C10.1, C11.2, C12.1, C13.1, C14.2, C15.2, C16.1, C17.1, C18.2, C19.1, C20.1, C21.1, C22.1, C23.1, C24.1, C25.1, C26.2, C27.2, C28.2, C29.1, C30.1, C31.1, C32.2, C33.1, C37.2, C38.2, C39.1, C40.1, C51.1, C55.1, C56.1, C57.2, C64.1, C65.1, C66.2, C67.1, C68.1, C69.1, C70.1, C71.2, C72.1, C73.1, C74.1, C75.1, C77.1, C78.2, C79.1, C81.2, C82.1, C83.1, C84.1, C85.1, C86.2, C87.2, CHARGING.4 (~CE), CHARGING.5 (EN2), CHARGING.8 (VSS), CHARGING.15 (TD), CHARGING.17 (EP), D1.3 (GND), ESD1.2 (GND), ESD2.2 (GND), ESD3.2 (GND), ESD4.2 (GND), ESD5.2 (GND), ESD6.2 (GND), ESD7.2 (GND), J3.5 (GND), R39.2, R49.2, R51.1, R53.1, R56.1, R58.2, R65.1, S1.3, U2.2 (-), VCC3.3_AN.2 (GND), VCC3.3_DIG.2 (GND)
AGND-SUBJECTGROUND: ESD7.1 (IO1), R45.1, SUBJECT_GND.MP
CS_ADC1: ADC3.18 (ALERT/!CS), BC832.A4 (P06)
CS_ADC2: ADC2.18 (ALERT/!CS), BC832.A5 (P08)
CS_ADC3: ADC1.18 (ALERT/!CS), BC832.C1 (P24)
DGND: ADC1.13 (MODE0/GPIO0), ADC1.14 (MODE1/GPIO1), ADC1.15 (MODE2/GPIO2), ADC1.16 (MODE3/ALERT), ADC1.22 (DGND), ADC1.31 (XTAL1), ADC1.56 (CLK_SEL), ADC2.13 (MODE0/GPIO0), ADC2.14 (MODE1/GPIO1), ADC2.15 (MODE2/GPIO2), ADC2.16 (MODE3/ALERT), ADC2.22 (DGND), ADC2.31 (XTAL1), ADC2.56 (CLK_SEL), ADC3.13 (MODE0/GPIO0), ADC3.14 (MODE1/GPIO1), ADC3.15 (MODE2/GPIO2), ADC3.16 (MODE3/ALERT), ADC3.22 (DGND), ADC3.31 (XTAL1), ADC3.56 (CLK_SEL), BC832.1 (GND), CLOCK.2 (GND), J1.3, J1.5, J1.9, R39.1, RESET.2
DRDY_ADC1: ADC3.30 (!DRDY), BC832.A2 (P17)
DRDY_ADC2: ADC2.30 (!DRDY), BC832.D4 (P14)
DRDY_ADC3: ADC1.30 (!DRDY), BC832.B1 (P25)
MEASURE_VBATM: ADC2.63 (AUXAIN+), R55.1, R56.2
MEASURE_VUSB: ADC1.63 (AUXAIN+), R49.1, R57.1
unnamed: ADC3.59 (AREG1CAP), C1.1
unnamed: ADC2.23 (DREGCAP), C12.2
unnamed: C22.2, D1.2 (OUT), R45.2
unnamed: C5.2, VCC3.3_DIG.4 (NR/FB)
unnamed: BC832.2 (P20/LED), LED1.1 (K)
unnamed: ADC3.63 (AUXAIN+), ADC3.64 (AUXAIN-)
unnamed: ADC3.51 (AREG2CAP), C7.1
unnamed: LED3.2 (A), R68.1
unnamed: LED1.2 (A), R69.1
unnamed: LED4.2 (A), R41.1
unnamed: ADC2.51 (AREG2CAP), C15.1
unnamed: ADC3.23 (DREGCAP), C14.1
unnamed: ADC1.23 (DREGCAP), C13.2
unnamed: LED2.2 (A), R43.1
unnamed: C57.1, VCC3.3_AN.4 (NR/FB)
unnamed: ADC1.59 (AREG1CAP), C32.1
unnamed: ADC2.59 (AREG1CAP), C26.1
unnamed: ADC1.51 (AREG2CAP), C18.1
unnamed: CHARGING.1 (TS), R62.1, R65.2
unnamed: CHARGING.16 (ISET), R53.2
unnamed: CHARGING.12 (ILIM), R51.2
P18/LED: BC832.5 (P18/LED), J1.6, LED3.1 (K)
POWERUP: S1.2, VCC3.3_AN.3 (EN), VCC3.3_DIG.3 (EN)
REF_ADC1: ADC3.8 (REF1+), ADC3.41 (REF2+), ADC3.49 (REF_OUT), C8.1, C21.2, C65.2, C70.2, C81.1
REF_ADC2: ADC2.8 (REF1+), ADC2.41 (REF2+), ADC2.49 (REF_OUT), C27.1, C29.2, C64.2, C71.1, C74.2
REF_ADC3: ADC1.8 (REF1+), ADC1.41 (REF2+), ADC1.49 (REF_OUT), C38.1, C51.2, C83.2, C85.2, C87.1
RESET: BC832.10 (P21/RESET), J1.10, RESET.1
RESET_ADC: ADC1.36 (!RESET), ADC2.36 (!RESET), ADC3.36 (!RESET), BC832.D1 (P23)
SDCLK: BC832.4 (SWCLK), J1.4
SDIO: BC832.3 (SWDIO), J1.2
SDI_ADC1: ADC3.20 (DCLK1/SDI), BC832.C4 (P15)
SDI_ADC2: ADC2.20 (DCLK1/SDI), BC832.B5 (P07)
SDI_ADC3: ADC1.20 (DCLK1/SDI), BC832.A1 (P28)
SDO_ADC1: ADC3.21 (DCLK0/SDO), BC832.D3 (P16)
SDO_ADC2: ADC2.21 (DCLK0/SDO), BC832.B4 (P05)
SDO_ADC3: ADC1.21 (DCLK0/SDO), BC832.B2 (P29)
SHIELD: J3.S4 (SHIELD), J3.S5 (SHIELD), J3.SH1 (SHIELD), J3.SH2 (SHIELD), J3.SH3 (SHIELD), J3.SH4 (SHIELD)
SLCK_ADC1: ADC3.19 (DCLK2/SCLK), BC832.A3 (P04)
SLCK_ADC2: ADC2.19 (DCLK2/SCLK), BC832.D2 (P19)
SLCK_ADC3: ADC1.19 (DCLK2/SCLK), BC832.C2 (P22)
START_ADC: ADC3.33 (!START), BC832.D5 (P10)
SYNC_ADC: ADC1.35 (!SYNC_IN), ADC2.35 (!SYNC_IN), ADC3.34 (!SYNC_OUT), ADC3.35 (!SYNC_IN)
USB_5VOLT+: CHARGING.13 (IN), J3.1 (VBUS), R57.2, R62.2
VCC3.3_AN: ADC1.6 (AVDD1A), ADC1.43 (AVDD1B), ADC1.52 (AVDD2B), ADC1.58 (AVDD2A), ADC1.62 (AVDD4), ADC2.6 (AVDD1A), ADC2.43 (AVDD1B), ADC2.52 (AVDD2B), ADC2.58 (AVDD2A), ADC2.62 (AVDD4), ADC3.6 (AVDD1A), ADC3.43 (AVDD1B), ADC3.52 (AVDD2B), ADC3.58 (AVDD2A), ADC3.62 (AVDD4), C2.2, C11.1, C16.2, C17.2, C23.2, C24.2, C25.2, C28.1, C30.2, C31.2, C37.1, C39.2, C40.2, C66.1, C67.2, C68.2, C69.2, C72.2, C73.2, C75.2, C77.2, C78.1, C79.2, C82.2, C84.2, C86.1, D1.1 (IN), ESD7.3 (IO2), R47.1, VCC3.3_AN.5 (OUT)
VCC3.3_DIG: ADC1.24 (IOVDD), ADC1.33 (!START), ADC1.54 (FORMAT1), ADC1.55 (FORMAT0), ADC2.24 (IOVDD), ADC2.33 (!START), ADC2.54 (FORMAT1), ADC2.55 (FORMAT0), ADC3.24 (IOVDD), ADC3.54 (FORMAT1), ADC3.55 (FORMAT0), BC832.16 (VDD), C3.2, C4.1, C6.1, C9.1, C10.2, C20.2, CLOCK.4 (VDD), ESD7.4 (IO3), J1.1, R68.2, R69.2, VCC3.3_DIG.5 (OUT)
VCC_BATTERY: C55.2, CHARGING.2 (BAT_2), CHARGING.3 (BAT), R55.2, U2.1 (+)
VIRTUAL_GND_PASSIVE: C33.2, R47.2, R58.1, SUBJECT_GND_VD.MP
V_OUT_CHARGER: C19.2, C56.2, CHARGING.6 (EN1), CHARGING.10 (OUT_2), CHARGING.11 (OUT), R41.2, R43.2, S1.1, VCC3.3_AN.1 (IN), VCC3.3_DIG.1 (IN)
XTAL_OUT: ADC1.32 (XTAL2/MCLK), ADC2.32 (XTAL2/MCLK), ADC3.32 (XTAL2/MCLK), CLOCK.3 (OUT)

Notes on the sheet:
Power Supply and Charging Circuit (configured to charge at 100mA max without tracking thermals of the battery)
POWER SUPPLY
Bluetooth

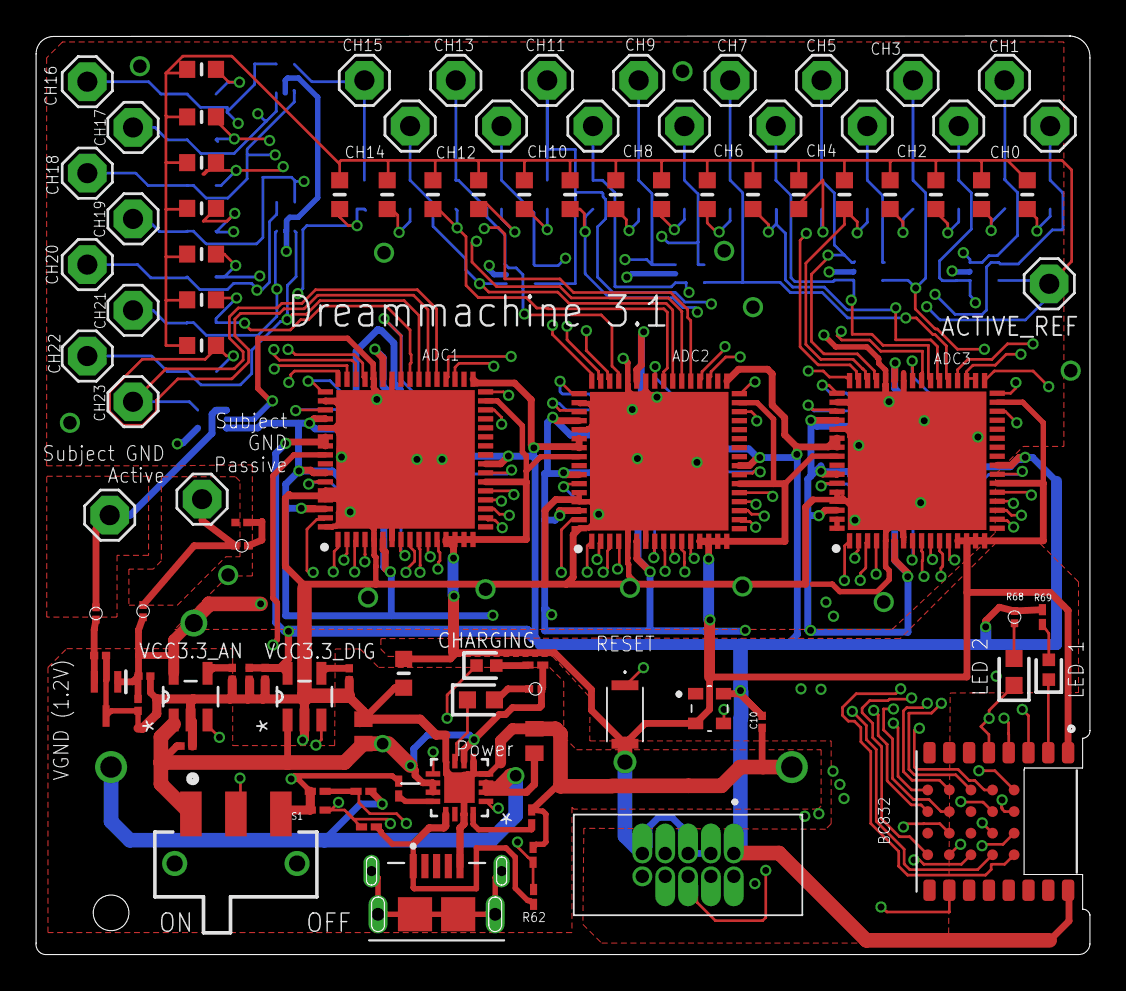
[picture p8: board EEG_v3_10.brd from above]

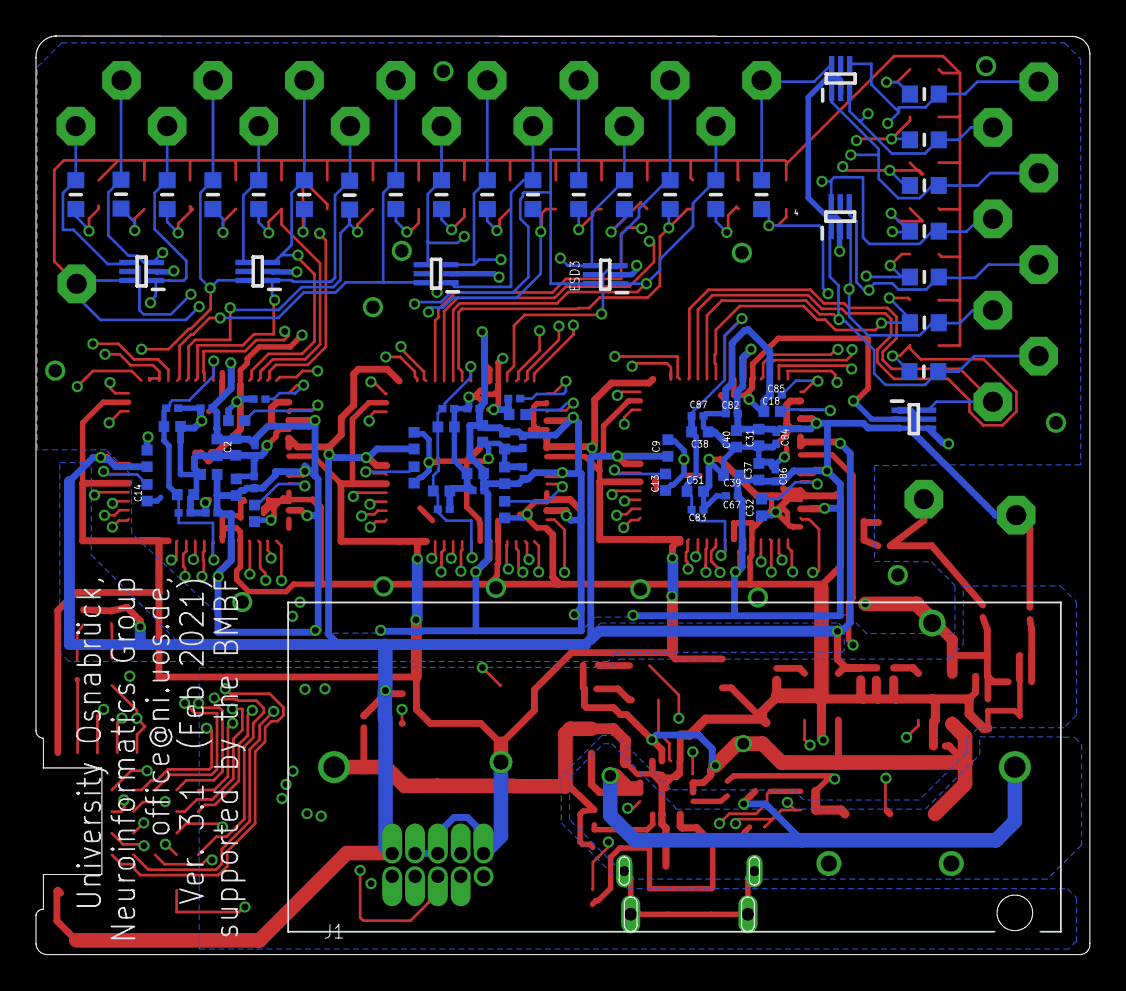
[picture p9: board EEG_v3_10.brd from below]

Board: 4 copper layers, 58.6 x 51.0 mm, 177 parts (82 on the bottom side), 110 nets.

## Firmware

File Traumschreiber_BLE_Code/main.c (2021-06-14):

/**
 * Copyright (c) 2014 - 2019, Nordic Semiconductor ASA
 *
 * All rights reserved.
 *
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
 * 3. Neither the name of Nordic Semiconductor ASA nor the names of its
 *    contributors may be used to endorse or promote products derived from this
 *    software without specific prior written permission.
 *
 * 4. This software, with or without modification, must only be used with a
 *    Nordic Semiconductor ASA integrated circuit.
 *
 * 5. Any software provided in binary form under this license must not be reverse
 *    engineered, decompiled, modified and/or disassembled.
 *
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
 */
/** @file
 *
 * @defgroup ble_sdk_app_template_main main.c
 * @{
 * @ingroup ble_sdk_app_template
 * @brief Template project main file.
 *
 * This file contains a template for creating a new application. It has the code necessary to wakeup
 * from button, advertise, get a connection restart advertising on disconnect and if no new
 * connection created go back to system-off mode.
 * It can easily be used as a starting point for creating a new application, the comments identified
 * with 'YOUR_JOB' indicates where and how you can customize.
 */

#include <stdbool.h>
#include <stdint.h>
#include <string.h>

#include "nordic_common.h"
#include "nrf.h"
#include "app_error.h"
#include "ble.h"
#include "ble_hci.h"
#include "ble_srv_common.h"
#include "ble_advdata.h"
#include "ble_advertising.h"
#include "ble_conn_params.h"
#include "nrf_sdh.h"
#include "nrf_sdh_soc.h"
#include "nrf_sdh_ble.h"
#include "app_timer.h"
#include "fds.h"
#include "peer_manager.h"
#include "peer_manager_handler.h"
#include "bsp_btn_ble.h"
#include "sensorsim.h"
#include "ble_conn_state.h"
#include "nrf_ble_gatt.h"
#include "nrf_ble_qwr.h"
#include "nrf_pwr_mgmt.h"

#include "nrf_log.h"
#include "nrf_log_ctrl.h"
#include "nrf_log_default_backends.h"

#include "traumschreiber_service.h"
#include "ad_spi.h"


#define DEVICE_NAME                     "Traumschreiber_v2"                     /**< Name of device. Will be included in the advertising data. */
#define MANUFACTURER_NAME               "IKW"                                   /**< Manufacturer. Will be passed to Device Information Service. */
#define APP_ADV_INTERVAL                300                                     /**< The advertising interval (in units of 0.625 ms. This value corresponds to 187.5 ms). */

#define APP_ADV_DURATION                18000                                   /**< The advertising duration (180 seconds) in units of 10 milliseconds. */
#define APP_BLE_OBSERVER_PRIO           3                                       /**< Application's BLE observer priority. You shouldn't need to modify this value. */
#define APP_BLE_CONN_CFG_TAG            1                                       /**< A tag identifying the SoftDevice BLE configuration. */

#define MIN_CONN_INTERVAL               MSEC_TO_UNITS(7.5, UNIT_1_25_MS)        /**< Minimum acceptable connection interval (0.1 seconds). */
#define MAX_CONN_INTERVAL               MSEC_TO_UNITS(11.25, UNIT_1_25_MS)        /**< Maximum acceptable connection interval (0.2 second). */
#define SLAVE_LATENCY                   20                                      /**< Slave latency. */
#define CONN_SUP_TIMEOUT                MSEC_TO_UNITS(3000, UNIT_10_MS)         /**< Connection supervisory timeout (4 seconds). */

#define FIRST_CONN_PARAMS_UPDATE_DELAY  APP_TIMER_TICKS(5000)                   /**< Time from initiating event (connect or start of notification) to first time sd_ble_gap_conn_param_update is called (5 seconds). */
#define NEXT_CONN_PARAMS_UPDATE_DELAY   APP_TIMER_TICKS(30000)                  /**< Time between each call to sd_ble_gap_conn_param_update after the first call (30 seconds). */
#define MAX_CONN_PARAMS_UPDATE_COUNT    3                                       /**< Number of attempts before giving up the connection parameter negotiation. */

#define SEC_PARAM_BOND                  1                                       /**< Perform bonding. */
#define SEC_PARAM_MITM                  0                                       /**< Man In The Middle protection not required. */
#define SEC_PARAM_LESC                  0                                       /**< LE Secure Connections not enabled. */
#define SEC_PARAM_KEYPRESS              0                                       /**< Keypress notifications not enabled. */
#define SEC_PARAM_IO_CAPABILITIES       BLE_GAP_IO_CAPS_NONE                    /**< No I/O capabilities. */
#define SEC_PARAM_OOB                   0                                       /**< Out Of Band data not available. */
#define SEC_PARAM_MIN_KEY_SIZE          7                                       /**< Minimum encryption key size. */
#define SEC_PARAM_MAX_KEY_SIZE          16                                      /**< Maximum encryption key size. */

#define DEAD_BEEF                       0xCAFFEBEE                              /**< Value used as error code on stack dump, can be used to identify stack location on stack unwind. */
//ODDBA11 CAFFEBEE


NRF_BLE_GATT_DEF(m_gatt);                                                       /**< GATT module instance. */
NRF_BLE_QWR_DEF(m_qwr);                                                         /**< Context for the Queued Write module.*/
BLE_ADVERTISING_DEF(m_advertising);                                             /**< Advertising module instance. */

static uint16_t m_conn_handle = BLE_CONN_HANDLE_INVALID;                        /**< Handle of the current connection. */

/* YOUR_JOB: Declare all services structure your application is using
 *  BLE_XYZ_DEF(m_xyz);
 */
ble_traum_t m_traum_service;

// OUR_JOB: Step 3.G, Declare an app_timer id variable and define our timer interval and define a timer interval
//APP_TIMER_DEF(m_traum_char_timer_id);
//#define TRAUM_CHAR_TIMER_INTERVAL     APP_TIMER_TICKS(500) // 1000 ms intervals


// YOUR_JOB: Use UUIDs for service(s) used in your application.
static ble_uuid_t m_adv_uuids[] =                                               /**< Universally unique service identifiers. */
{
    {BLE_UUID_TRAUM_SERVICE, BLE_UUID_TYPE_BLE},
	{BLE_UUID_DEVICE_INFORMATION_SERVICE, BLE_UUID_TYPE_BLE}
};


static void advertising_start(bool erase_bonds);


/**@brief Callback function for asserts in the SoftDevice.
 *
 * @details This function will be called in case of an assert in the SoftDevice.
 *
 * @warning This handler is an example only and does not fit a final product. You need to analyze
 *          how your product is supposed to react in case of Assert.
 * @warning On assert from the SoftDevice, the system can only recover on reset.
 *
 * @param[in] line_num   Line number of the failing ASSERT call.
 * @param[in] file_name  File name of the failing ASSERT call.
 */
void assert_nrf_callback(uint16_t line_num, const uint8_t * p_file_name)
{
    app_error_handler(DEAD_BEEF, line_num, p_file_name);
}


/**@brief Function for handling Peer Manager events.
 *
 * @param[in] p_evt  Peer Manager event.
 */
static void pm_evt_handler(pm_evt_t const * p_evt)
{
    pm_handler_on_pm_evt(p_evt);
    pm_handler_flash_clean(p_evt);

    switch (p_evt->evt_id)
    {
        case PM_EVT_PEERS_DELETE_SUCCEEDED:
            advertising_start(false);
            break;

        default:
            break;
    }
}


/**@brief Function for the Timer initialization.
 *
 * @details Initializes the timer module. This creates and starts application timers.
 */
static void timers_init(void)
{
    // Initialize timer module.
    ret_code_t err_code = app_timer_init();
    APP_ERROR_CHECK(err_code);

}


/**@brief Function for the GAP initialization.
 *
 * @details This function sets up all the necessary GAP (Generic Access Profile) parameters of the
 *          device including the device name, appearance, and the preferred connection parameters.
 */
static void gap_params_init(void)
{
    ret_code_t              err_code;
    ble_gap_conn_params_t   gap_conn_params;
    ble_gap_conn_sec_mode_t sec_mode;

    BLE_GAP_CONN_SEC_MODE_SET_OPEN(&sec_mode);

    err_code = sd_ble_gap_device_name_set(&sec_mode,
                                          (const uint8_t *)DEVICE_NAME,
                                          strlen(DEVICE_NAME));
    APP_ERROR_CHECK(err_code);

    /* YOUR_JOB: Use an appearance value matching the application's use case.
       err_code = sd_ble_gap_appearance_set(BLE_APPEARANCE_);
       APP_ERROR_CHECK(err_code); */

    memset(&gap_conn_params, 0, sizeof(gap_conn_params));

    gap_conn_params.min_conn_interval = MIN_CONN_INTERVAL;
    gap_conn_params.max_conn_interval = MAX_CONN_INTERVAL;
    gap_conn_params.slave_latency     = SLAVE_LATENCY;
    gap_conn_params.conn_sup_timeout  = CONN_SUP_TIMEOUT;

    err_code = sd_ble_gap_ppcp_set(&gap_conn_params);
    APP_ERROR_CHECK(err_code);
}


/**@brief Function for initializing the GATT module.
 */
static void gatt_init(void)
{
    ret_code_t err_code = nrf_ble_gatt_init(&m_gatt, NULL);
    APP_ERROR_CHECK(err_code);

    //enable larger packet sizes
//    uint16_t dummy = nrf_ble_gatt_eff_mtu_get(&m_gatt, 0);
    err_code = nrf_ble_gatt_att_mtu_periph_set(&m_gatt, BLE_TRAUM_ATT_MTU);
    APP_ERROR_CHECK(err_code);
//    uint8_t dummy2;
//    err_code = nrf_ble_gatt_data_length_get(&m_gatt, BLE_CONN_HANDLE_INVALID, &dummy2);
    err_code = nrf_ble_gatt_data_length_set(&m_gatt, BLE_CONN_HANDLE_INVALID, BLE_TRAUM_GAP_DL);
    APP_ERROR_CHECK(err_code);
}


/**@brief Function for handling Queued Write Module errors.
 *
 * @details A pointer to this function will be passed to each service which may need to inform the
 *          application about an error.
 *
 * @param[in]   nrf_error   Error code containing information about what went wrong.
 */
static void nrf_qwr_error_handler(uint32_t nrf_error)
{
    APP_ERROR_HANDLER(nrf_error);
}


/**@brief Function for initializing services that will be used by the application.
 */
static void services_init(void)
{
    ret_code_t         err_code;
    nrf_ble_qwr_init_t qwr_init = {0};

    // Initialize Queued Write Module.
    qwr_init.error_handler = nrf_qwr_error_handler;

    err_code = nrf_ble_qwr_init(&m_qwr, &qwr_init);
    APP_ERROR_CHECK(err_code);

    traum_service_init(&m_traum_service);

}


/**@brief Function for handling the Connection Parameters Module.
 *
 * @details This function will be called for all events in the Connection Parameters Module which
 *          are passed to the application.
 *          @note All this function does is to disconnect. This could have been done by simply
 *                setting the disconnect_on_fail config parameter, but instead we use the event
 *                handler mechanism to demonstrate its use.
 *
 * @param[in] p_evt  Event received from the Connection Parameters Module.
 */
static void on_conn_params_evt(ble_conn_params_evt_t * p_evt)
{
    ret_code_t err_code;

    if (p_evt->evt_type == BLE_CONN_PARAMS_EVT_FAILED)
    {
        err_code = sd_ble_gap_disconnect(m_conn_handle, BLE_HCI_CONN_INTERVAL_UNACCEPTABLE);
        APP_ERROR_CHECK(err_code);
    }
}


/**@brief Function for handling a Connection Parameters error.
 *
 * @param[in] nrf_error  Error code containing information about what went wrong.
 */
static void conn_params_error_handler(uint32_t nrf_error)
{
    APP_ERROR_HANDLER(nrf_error);
}
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

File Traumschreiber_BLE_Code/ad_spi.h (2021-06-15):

/**
 * Copyright (c) 2015 - 2019, Nordic Semiconductor ASA
 *
 * All rights reserved.
 *
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
 * 3. Neither the name of Nordic Semiconductor ASA nor the names of its
 *    contributors may be used to endorse or promote products derived from this
 *    software without specific prior written permission.
 *
 * 4. This software, with or without modification, must only be used with a
 *    Nordic Semiconductor ASA integrated circuit.
 *
 * 5. Any software provided in binary form under this license must not be reverse
 *    engineered, decompiled, modified and/or disassembled.
 *
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
 */

 #ifndef AD_SPI_H_
#define AD_SPI_H_


#include "nrf_drv_spi.h"
#include "app_util_platform.h"
#include "nrf_gpio.h"
#include "nrf_drv_gpiote.h"
#include "nrf_delay.h"
#include "boards.h"
#include "app_error.h"
#include <string.h>
#include "nrf_log.h"
#include "nrf_log_ctrl.h"
#include "nrf_log_default_backends.h"
#include "app_timer.h"
#include "nrf_drv_timer.h"
#include "traumschreiber_service.h"

#define ARM_MATH_CM4
#include "arm_math.h"




#define SPI_0_DRDY 17 // connected to \DRDY-signal from AD0
#define SPI_0_SCLK  4 // connected to SCLK-signal from AD0
#define SPI_0_CS    6 // connected to CS-signal from AD0
#define SPI_0_SDI  15 // connected to SDI-signal from AD0
#define SPI_0_SDO  16 // connected to SDO-signal from AD0

#define SPI_1_DRDY 14 // connected to \DRDY-signal from AD1
#define SPI_1_SCLK  19 // connected to SCLK-signal from AD1
#define SPI_1_CS    8 // connected to CS-signal from AD1
#define SPI_1_SDI  7 // connected to SDI-signal from AD1
#define SPI_1_SDO  5 // connected to SDO-signal from AD1

#define SPI_2_DRDY 25 // connected to \DRDY-signal from AD2
#define SPI_2_SCLK  22 // connected to SCLK-signal from AD2
#define SPI_2_CS    24 // connected to CS-signal from AD2
#define SPI_2_SDI  28 // connected to SDI-signal from AD2
#define SPI_2_SDO  29 // connected to SDO-signal from AD2

#define AD_NUMBER      3
static const uint8_t spi_instances[] = {0,1,2}; /**< SPI instance indices. */
static uint8_t spi_instances_id[] = {0,1,2}; /**< SPI instance indices for ini-funcion callback context (needs to be !const). */
static const nrf_drv_spi_t spi[] = {NRF_DRV_SPI_INSTANCE(0), NRF_DRV_SPI_INSTANCE(1), NRF_DRV_SPI_INSTANCE(2)};  /**< SPI instance. */

//#define SPI_INSTANCE  0 /**< SPI instance index. */
//static const nrf_drv_spi_t spi = NRF_DRV_SPI_INSTANCE(SPI_INSTANCE);  /**< SPI instance. */


//SPI Constants and buffers
#define SPI_READ_SIGNAL   {0x80, 0x00, 0x00, 0x00, 0x00, 0x00, 0x00, 0x00, 0x00, 0x00, 0x00, 0x00, 0x00, 0x00, 0x00, 0x00, 0x00, 0x00, 0x00, 0x00, 0x00, 0x00, 0x00, 0x00, 0x00, 0x00, 0x00, 0x00, 0x00, 0x00, 0x00, 0x00} //default read signal for 32 Bytes
#define SPI_READ_CHANNEL_NUMBER   8
#define SPI_CHANNEL_NUMBER_TOTAL SPI_READ_CHANNEL_NUMBER*AD_NUMBER
#define SPI_READ_PER_CHANNEL      4
#define SPI_READ_LENGTH   SPI_READ_CHANNEL_NUMBER*SPI_READ_PER_CHANNEL
static uint8_t       m_tx_buf[] = SPI_READ_SIGNAL;           /**< TX buffer. */
static uint8_t       m_rx_buf[AD_NUMBER][SPI_READ_LENGTH + 1];    /**< RX buffer. */
static const uint8_t m_length  =  sizeof(m_tx_buf);        /**< Transfer length. */
static const uint8_t m_rlength =  sizeof(m_rx_buf[0]);        /**< RX Buffer length. */
static uint8_t bat_tx_buf[8] = {0}; //buffer for battery read spi transfer
static const uint8_t spi_ad_battery = 1; //AD number of the AD the battery voltage is connected to
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

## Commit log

2020-03-26 Order Version
    [Changes.xlsx, EEG_v2_0.brd, EEG_v2_0.csv, EEG_v2_0.sch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]
2020-04-09 Add sockets test
2020-05-13 Update working prototype
2020-05-29 Final Version 2.8
    Update V 2.8 - Order Board design
    [Changes.xlsx, EEG_v2_0.brd, EEG_v2_0.csv, EEG_v2_0.sch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]
2020-05-31 new version after 2.8
    [EEG_v2_8.brd, EEG_v2_8.sch, EEG_v2_8b.brd, EEG_v2_8b.csv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]
2020-06-17 Added the app in a new folder with some minor changes for the connection with the new Traumschreiber and the decoding according to the decoding manual, still needs to be included correctly
    [eeg_data.csv]
2020-07-10 DataFiles and first analysis
    Contains the FIles evaluating the device noise (of function generator) and Traumschreiber and a first version of the analysis.
    [20200709-11h57EEGrecording.csv, 20200709-12h01EEGrecording.csv, 20200709-12h04EEGrecording.csv, 20200709-12h12EEGrecording.csv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]
2020-07-16 Canged vendor_prefix
    Prior version does not work for all TS, now, all BT devices are shown in list
    [16-07-2020_13-31-18_test2.csv]
2020-07-16 Tried to adapt to new data format
    [test2.csv]
2020-07-17 Files from today's experiment.
    Documentation will follow
    [16-07-2020_15-01-54_Exp1.csv, 16-07-2020_15-08-33_Exp1_1.csv, 16-07-2020_15-12-09_Exp2.csv, 16-07-2020_15-14-43_Exp3.csv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]
2020-07-20 Automated and cleaned up plotting
    All csv files are now cleaned uo and plotted automatically. Old datafiles removed and plots included
    [16-07-2020_15-01-54_Exp1.csv, 17-07-2020_16-12-52_Exp27.csv, 20200709-11h57EEGrecording.csv, 20200709-12h01EEGrecording.csv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]
2020-07-22 Unify EEGDroid code
    [eeg_data.csv]
2020-07-29 Rewrite socket as websocket
2020-07-29 Update submodule, rewrite socket as websocket
2020-08-17 SanityCheck5 Analysis
    Added the recent Sanity Check data and cleaned up the prior data a bit
    [16-07-2020_13-31-18_test2.csv, 16-07-2020_15-08-33_Exp1_1.csv, 16-07-2020_15-12-09_Exp2.csv, 16-07-2020_15-14-43_Exp3.csv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]
2020-08-24 Sanity Check 6 data
    [24-08-2020_12-23-32_exp1.csv, 24-08-2020_12-34-13_exp2 .csv, 24-08-2020_12-35-12_exp3.csv, 24-08-2020_12-38-40_exp4.csv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]
2020-08-25 cleaned up directory, added support for half sampled/half generated data
2020-09-01 Analysis of jumps I
    Added an analysis of the jumps and cleaned some code. Not a lot though
    [24-08-2020_12-23-32_exp1.csv, 24-08-2020_13-02-03_exp25.csv, 24_1.csv, 24_2.csv]
2020-09-05 changed data flow, fixed notify ack bug, added battery check
    data flow changed to encode on data receive, dropped one ring buffer
    fixed notification acknowledgment bug due to configuration characteristic
    added battery check via config characteristic (sends dummy data for now, due to unresolved spi bug)
2020-09-09 implemented IIR filtering
    included biquad cascade iir filter from arm_math package
2020-09-10 My work on the app analysis
    [02-09-2020_15-24-42_test.csv]
2020-09-10 2 small bug fixes
    wrong sdk_config file
    iir filter coeffs updated for 250Hz
2020-09-10 fixed Byte order mix-up due to filtering
2020-09-15 implemented sending on 3 characteristics
    also disabled dummy data filtering
2020-10-05 Notebooks for analysing lost packages
    [02-09-2020_15-24-42_test.csv, 10-09-2020_14-45-50_exp1.csv, 10-09-2020_14-54-01_exp2.csv, 10-09-2020_15-42-20_exp3 .csv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]
2020-10-07 added dcpm
    24 channels with 10Bit difference values each
    1 sample (24 channels) is send via 1.5 packages
    sampling at 167Hz
    sending packages at 250Hz
2021-01-07 slowing last quickfix and optimising variance calculation
    2min30-bug should be fixed now. buffer capacity calculation was changed for this
    variance calculation now has outsider handling
2021-01-22 code restructuring/cleaning, added battery monitoring
    program flow was adapted for better interrupt handling
    battery status readout happens at connection event and recording stop (is written in config characteristic)
2021-02-12 filtering update
    added low pass filter
    notch filter switched to 500Hz (and averaging after)
    coefficients changeable via config char
2021-02-16 switching out some filters
2021-02-19 added high pass filter and running average calculation
2021-02-23 added first order high pass filter option
2021-03-01 new filter and config structure
2021-03-02 changes on filters, running average, encoding updates
    high pass filtering now @ 167Hz
    running average maybe fixed, still disabled
    encoding updates have priority over regular packages
2021-03-22 ordered
    ordered version
    [EEG_v2_92_X25.brd, EEG_v2_92_X25.sch, EEG_v3_10.brd, EEG_v3_10.csv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]
2021-05-11 0.3.5 filters for 250Hz added
2021-05-18 0.3.6 transmission @ 167/250Hz switchable
2021-06-09 Removed old code
    Clean up repo by deleting old code (stored locally too)
    [10-09-2020_14-45-50_exp1.csv, 10-09-2020_14-54-01_exp2.csv, 10-09-2020_15-42-20_exp3 .csv, 10-09-2020_15-42-57_exp4.csv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]
2021-06-14 0.3.8 event length change and battery fix
2021-06-15 0.3.9 another battery fix
